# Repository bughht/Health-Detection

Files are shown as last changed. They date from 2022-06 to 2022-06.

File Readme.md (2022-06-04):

# 健康检测手环/手套
**一、项目的实施方案**

设计一个基于加速度传感器、陀螺仪、薄膜压力传感器、血氧传感器，开发可用于老龄化疾病(帕金森等)检测以及血氧饱和度等生理参数检测的系统。

设想1：老年人监测摔倒

当老年人遇到意外情况时,如果老年人质心位置—速度状态不在动态稳定区域以内(稳度为负)，老年人就会不稳定而失去平衡，对于老年人，下肢肌力衰退会导致下肢支撑力不够,不足以支撑起老年人在跌倒时导致的身体下降；同时由于老年人神经系统控制能力下降,神经传导减慢，动作反应时间延长,也会导致老年人在发生跌倒时不能及时的调整身体以保持平衡。

`	`老年人发生摔倒的过程中包括初始安全状态、失重状态、与低势物体或地面的撞击状态和倒后的平稳状态。其身体的三轴合加速度值定义为a=ax2+ay2+az2。在正常情况下，使用者的加速度值并不会有大的变化。但在失重状态和撞击状态，老年人的躯干三轴合加速度值a的变化很大。在日常生活中，人的上躯体部分的运动幅度较小，加速度变化不大，而在摔倒过程中，运动幅度变大，加速度变化很大。因此，三轴加速度传感器安装在老年人的上躯干部分。

设想2：帕金森监测

在出现帕金森之后，一些老年人的手脚会出现颤抖的情况，机械振荡是最简单导致震颤的原因，观察一个伸展的肢体如手，伸肌被激活去拮抗重力，而伸肌的激活又会导致拮抗它的屈肌激活，这样手部的肌纤维就会按照一个既定的频率被激活，因此手会依照一个既定的频率振荡，而这个频率在身体的不同部位是不同的，例如在手指是25Hz，手腕是6~8Hz，肘部是3~4Hz，而肩关节则是0.5~2Hz，这种频率会因为重量的加大而减低，或者紧张度的加大而增高。

用集成了三轴加速度计和陀螺仪的MPU-6050芯片采集手腕三轴加速度和角度，主要通过分析手腕三轴角度变化来判断穿戴者是否具有帕金森症状以及症状的严重程度。

设想3：血氧饱和度监测
`	`血氧饱和度是血液中被氧结合的氧合血红蛋白（HbO2）的容量占全部可结合的血红蛋白（Hb）容量的百分比，即血液中血氧的浓度，是呼吸循环的重要生理参数之一。如果血氧含量低，容易引发疲劳易困、精力不足、记忆力下降等状况，长期的血氧含量不足，还会对大脑、心脏等器官造成伤害。特别对于老年人，应每天监测血氧含量，一旦血氧低于警戒水平，需尽快补氧。
`	`测量时，需将血氧传感器紧贴皮肤。因为携带氧气的红血球能吸收较多红外光（850-1000mm），未携带氧气的红血球则是吸收较多的红光（600-750mm）。所以一般是通过测量双光束吸光度变化之比，一般选择入射光波长为660nm和940nm。运用Lambert-Bear定律并根据氧饱和度的定义可推出动脉血氧饱和度的近似公式为：Sa02=abQ。式中：Q为两种波长(Hb02、Hb)的吸光度变化之比a、b为常数，与仪器传感器结构、测量条件有关。 

**二、项目的核心器件**

**1.esp32开发板**

ESP-WROOM-32是一款通用型WiFi-BT-BLE MCU模组，功能强大，用途广泛。
`	`此款模组的核心是ESP32芯片，具有可扩展、自适应的特点。两个CPU核可以被单独控制或上电。时钟频率的调节范围为80MHz到240MHz。用户可以切断CPU的电源，利用低功耗协处理器来不断地监测外设的状态变化或某些模拟量是否超出阈值。ESP32还集成了丰富的外设，包括电容式触摸传感器、霍尔传感器、低噪声传感放大器，SD卡接口、以太网接口、高速SDIO／SPI、UART、I2S和I2C等。
`	`ESP-WROOM-32集成了传统蓝牙、低功耗蓝牙和Wi-Fi，具有广泛的用途：Wi-Fi支持极大范围的通信连接，也支持通过路由器直接连接互联网；而蓝牙可以让用户连接手机或者广播BLE Beacon以便于信号检测。ESP32芯片的睡眠电流小于5mA，使其适用于电池供电的可穿戴电子设备。ESP-WROOM-32支持的数据传输速率高达150Mbps，经过功率放大器后，输出功率可达到22dBm，可实现大范围的无线通信。因此，这款芯片拥有领先的技术规格，在高集成度、无线传输距离、功耗以及网络联通等方面性能佳。
`	`ESP32的操作系统是带有LWIP的freeRTOS，还内置了带有硬件加速功能的TLS1.2。芯片同时支持OTA加密升级。

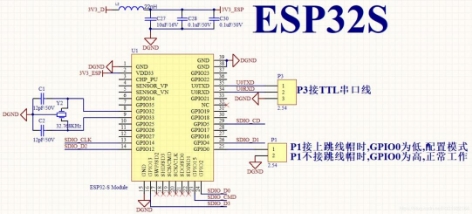
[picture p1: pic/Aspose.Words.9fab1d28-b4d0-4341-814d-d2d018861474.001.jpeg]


esp32电路图

2. **MPU6050**

MPU-60X0是世界上第一款集成 6 轴MotionTracking设备。它集成了3轴MEMS陀螺仪，3轴MEMS加速度计，以及一个可扩展的数字运动处理器 DMP（ DigitalMotion Processor），可用I2C接口连接一个第三方的数字传感器，比如磁力计。扩展之后就可以通过其 I2C或SPI接口输出一个9轴的信号（ SPI接口仅在MPU-6000可用）。 MPU-60X0也可以通过其I2C接口连接非惯性的数字传感器，比如压力传感器。
`	`MPU-60X0对陀螺仪和加速度计分别用了三个16位的ADC，将其测量的模拟量转化为可输出的数字量。为了精确跟踪快速和慢速的运动，传感器的测量范围都是用户可控的，陀螺仪可测范围为±250， ±500， ±1000， ±2000°/秒（ dps），加速度计可测范围为±2， ±4，±8， ±16g。
`	`MPU6050是一个比较常见的“陀螺仪”，实际上它不仅包含三轴陀螺仪，还包含了三轴加速度计。MPU6050是一个典型的MEMS，将六轴的东西集成到了大概3mm×3mm×1.5mm的体积之中，因此在飞控中得到广泛应用。

MPU6050使用I2C进行通信。I2C使用两条线SCL、SDA进行通信，再加上供电的两条线，使用MPU6050仅需要电源、GND、SCL、SDA即可。

其他引脚:

· XCL、XDA,一般是接其他I2C器件，如磁力计等，然后通过编程，可以让MPU6050帮你读取磁力计的数据，再一起读回单片机。

·IRQ，中断引脚，可以编程设定当数据准备好时，该引脚有电平变化，触发单片机的外部中断。

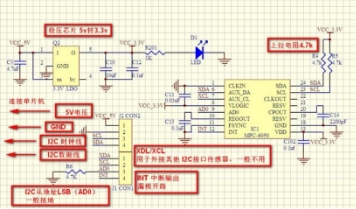
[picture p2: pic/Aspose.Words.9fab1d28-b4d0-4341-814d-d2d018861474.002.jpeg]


MPU6050电路图

**3.MAX30100**

MAX30100是一款集成有脉搏血氧仪和心率监测传感器的模块。该器件集成有两个LED、一个光电探测器，经过优化的光学器件和低噪声模拟信号处理器，可检测脉搏血氧及心率信号。MAX30100采用1.8V和3.3V的电源电压。可通过软件来关断电源，待机模式下的电流消耗量可忽略不计，因而可以始终保持电源连接。并且MAX30100采用I2C通信方式。

采集过程：RED和IR照射然后使用ADC进行数据采集，采集后的AD值经过数字滤波器进入数据寄存器，然后使用IIC进行数据采集，在转换AD值时，也可以采集温度值。

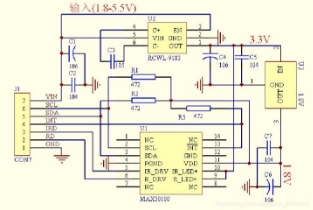
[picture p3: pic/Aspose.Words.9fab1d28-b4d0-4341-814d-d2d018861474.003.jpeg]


MAX30100电路图

**三、项目的制作过程**

考虑到手背血管相对贴近皮肤，有利于血氧传感器的监测，并且对于老年人手部帕金森震颤的监测更为容易，而若监测器件便于拆解，则可以让老人在出门时携带该器件以便监测老人在外是否摔倒，并在摔倒情况发生后尽快通知监护人，同时警示周围人群。

为了将上述方案融入一个检测系统中，且适合老人使用，我们决定制作一个可拆解的可穿戴式手部护具。

我们先进行硬件模块的设计与制作。为了实现我们预想的功能，我们首先选择并购置了相应的传感器；选用MPU6050收集使用者手部发生帕金森震颤时的三轴加速度和角度数据；用MAX30100检测使用者的血氧饱和度和体温；用薄膜压力传感器试图检测使用者手部挥动时对护具产生的压力，并与所测的三轴加速度和角度结合分析使用者是否摔倒。

一开始我们使用stm32进行环境开发，但由于需要与各模块相连接且需要将检测的数据传输到上位机，我们碰到了一些较难解决的问题，最后决定使用esp32开发环境。esp32开发板集成了蓝牙和WIFI传输数据的功能，简化了一些繁琐的配置步骤。理论上需要3.3V的电压供电，驱动各模块正常运行，但esp32自带前置降压，我们额外增加了一个升压模块将电源电压升高，再由esp32自己降到3.3V为各模块供电。

选择好各种传感器与开发板后，接下来就是将它们组装起来。利用I2C总线将各个模块与esp32进行连接。在实际焊接前，我们先在洞洞板上将各模块连接起来进行测试，得到了较为理想的结果。由于不会制作PCB板，在实际焊接过程中只能使用跳线将各模块进行连接。然而我们发现在实际焊接中并不能得到所预想的检测结果。经过检查发现是因为各模块是用导线进行连接的，导线较长对I2C会有较大的干扰。最终我们将导线剪短并加上了相应的上拉电阻，解决了此问题，成功将开发板与各模块相连。

1316718546-272481763-815E5E48DF970293284955976F0000EF

硬件各模块连接图

内部电路基本制作完成后，我们还需要设计一个外壳。起初，我们打算制作一个具有检测功能的手套，手腕部安装显示屏和血氧传感器，其余电路安置在手套的手背位置，仔细考虑一番觉得这样的设计不具有美观性且不切实际，最关键的是电路手背部分电路容易损坏，最终决定将所有电路全部装载在一个3D打印的外壳中，尽管这样的设计使成品看起来有一点笨重，但一体化设计使其具有很大的灵活性，不仅可以与各种模具结合以手表、护手等形式使用，也可以拆卸下来随身携带。

软件部分，我们起初打算采集到一个数据便将它传送至上位机处理，但由于我们之前将几个模块都连接在了I2C总线上，I2C是低速线，无法做到数据快速采集并传输。所以我们改为一帧里几个传感器同时采集数据，采集完将数据一起传输到上位机，但要提高采样率，保证较快的数据传输速度。处理采集到的数据时，我们使用了MATLAB，该软件运行处理较为缓慢，对我们项目正常的实施过程有一定的影响。

4. **项目的结果分析**

1.硬件电路板部分

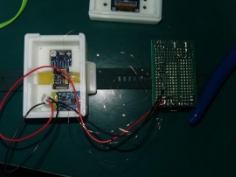
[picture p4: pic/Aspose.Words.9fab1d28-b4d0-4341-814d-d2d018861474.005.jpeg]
EA326454065DDD6A7FE0F28A32361031
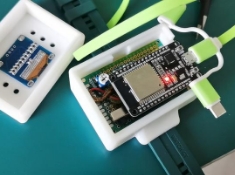
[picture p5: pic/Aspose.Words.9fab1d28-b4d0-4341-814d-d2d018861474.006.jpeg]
271CA8FF180BEBAEB58ACFB6554CEB21
       

2.最终成品分三段发送由三个模块采集的数据，每段128帧，第一段是由MPU6050采集的三轴加速度，使用卡尔曼计算姿态角，第二段使用MAX30100采集并计算血氧数据，第三段使用压力传感器采集施加至其上的压力，最后通过蓝牙将三段数据依次发送至上位机。

![1}4]48WX{49F(1C~1GFFUGF](pic/Aspose.Words.9fab1d28-b4d0-4341-814d-d2d018861474.007.jpeg)

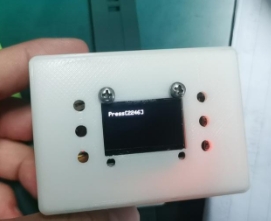
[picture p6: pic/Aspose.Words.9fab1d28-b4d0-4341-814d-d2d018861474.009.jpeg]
V60YQ6VU4)~8Q~AO)1K{V\_U
![5YYLY@]YP\_B7X8CJ}GT56LF](pic/Aspose.Words.9fab1d28-b4d0-4341-814d-d2d018861474.008.jpeg)   

3.当UI界面开始运行，点击开始检测，上位机程序会开放蓝牙接口并开始接收由硬件采集到的数据，并通过对采集到的数据进行分析，尽可能达到我们的设计目标。首先，当数据传输至上位机后对其进行分段处理，通过检测第一段采集到的加速度信号的过零率来分析佩戴者手部的震颤程度，以判断佩戴者手部是否出现类似帕金森的症状，并在界面右侧的静态文本框中显示“有帕金森吗小老弟”。通过对第二段采集到的血氧信号进行处理，得到佩戴者的血氧饱和度并对其频谱进行分析并显示至右侧上方两个坐标区中，同时，如果佩戴者的血氧不在阈值范围内，则判断佩戴者未正确佩戴手环，并显示在界面右侧第二个静态文本框中。对采集到的第三段压力数据进行处理并显示其频谱数据。

BC3344DD675796D992E37C8521789DD1

4. **总结与展望**

我们这次做出的成品总体来说还有许多不足之处，比如说预计的老人摔倒警报功能，由于我们的设计中是分三段采集和发送数据，而老人的摔倒是一个短时过程，可能老人摔倒时设备正好没有在监测老人的运动姿态，导致数据没有能够及时记录和传输，无法报警；同时我们还有能够计算温度的模块，但由于所需测定时间过长且干扰严重从而删除了该功能。

对于血氧数据的降噪技术也是一个难点，采集到的血氧数据没有得到很好的降噪，只能在比较严苛的操作情况下能看到有规律的qrs波尖峰上部图像，无法准确的计算心率。压力传感器的敏感度也偏低，没有达到预想的效果。

但是，从目前已实现的效果来看，它成功的发挥了一个帕金森手部震颤监测器的效果，且能够大致地测定使用者常态下的血氧饱和度，便携程度也达到了预想的标准，是一款兼具了巨大开发潜力和实用性为一身的作品。

在此基础上，我们对其更多功能的综合与优化也有其设想，例如：老年人可能出现记忆力降低或者患有老年痴呆的疾病，会有走失的风险。我们之后也可以在穿戴式设备上增加GPS实时定位的技术，随时了解老年人所在的位置。老年人身体机能下降，容易摔倒或突发某些疾病，出现上述情况时，不光通过警报通知周围人群，家属也可以及时定位到老人的所在位置。在表带附近增设血压监测传感器，及时发现老人的血压变动，提醒老人或其监护人及时服药或就医。

我们相信，如果能够继续优化开发，解决目前已发现的种种难题，那么，这将是一个兼具低成本、低使用要求、高效且实用的老年人监护辅助设备。	

**六、参考文献**

[1] 王亚宾,张小栋,穆小奇,韩焕杰.用于助老伴行机器人的老年人摔倒预测方法研究[J].电子测量与仪器学报,2018,32(07):1-7.

[2] Castiglia S F, Tatarelli A, Ranavolo A, et al. Ability of a set of trunk acceleration-derived 

gait stability indexes to identify gait unbalance and recurrent fallers in subjects with Parkinson's 

disease[J]. Journal of the Neurological Sciences, 2021, 429.

[3] 吴小玲,蔡桂艳.可穿戴式血氧传感器的设计和定标方法研究[J].生物医学工程学杂志,2009,26(04):731-734+738.

[4] 周一峰,刘超英,黄虎,郭一鸣,邹林方.基于光电容积脉搏波描记法的反射型PPG信号传感器的设计[J].电子世界,2016(12):161.

[5]       Zhou C, Yang L, Liao H, et al. Ankle foot motion recognition based on wireless wearable 

sEMG and acceleration sensors for smart AFO[J]. Sensors and Actuators A: Physical, 2021, 331: 113025.

[6] 吴天昊. 基于3轴加速度传感器及陀螺仪的老年人摔倒识别[D].北京工业大学,2013.

[7] Zhang Xiaodong,Wang Yunxia,Wei Xiaojuan.Research on control technology of elderly-assistant & walking-assistant robot based on tactile-slip sensation[J].Engineering Sciences,2013,11(01):89-96.

5

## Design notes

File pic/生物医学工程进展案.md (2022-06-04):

《生物医学工程进展A》课程项目

实施报告

题		 目：       穿戴式老年人生理参数检测设备     

组    号：                    1                   

任课教师：                 蒋皆恢                 

组    长： 19120318   洪浩天    24%               

成    员： 18121791   郭嘉      19%              

成    员： 19121718   詹美静    19%               

成    员： 19123227   刘奕欣    19%               

成    员： 19123248   胡悦滢    19%               

联系方式：            15800737097                 

二零二一年十一月九日 

**一、项目的实施方案**

设计一个基于加速度传感器、陀螺仪、薄膜压力传感器、血氧传感器，开发可用于老龄化疾病(帕金森等)检测以及血氧饱和度等生理参数检测的系统。

设想1：老年人监测摔倒

当老年人遇到意外情况时,如果老年人质心位置—速度状态不在动态稳定区域以内(稳度为负)，老年人就会不稳定而失去平衡，对于老年人，下肢肌力衰退会导致下肢支撑力不够,不足以支撑起老年人在跌倒时导致的身体下降；同时由于老年人神经系统控制能力下降,神经传导减慢，动作反应时间延长,也会导致老年人在发生跌倒时不能及时的调整身体以保持平衡。

`	`老年人发生摔倒的过程中包括初始安全状态、失重状态、与低势物体或地面的撞击状态和倒后的平稳状态。其身体的三轴合加速度值定义为a=ax2+ay2+az2。在正常情况下，使用者的加速度值并不会有大的变化。但在失重状态和撞击状态，老年人的躯干三轴合加速度值a的变化很大。在日常生活中，人的上躯体部分的运动幅度较小，加速度变化不大，而在摔倒过程中，运动幅度变大，加速度变化很大。因此，三轴加速度传感器安装在老年人的上躯干部分。

设想2：帕金森监测

在出现帕金森之后，一些老年人的手脚会出现颤抖的情况，机械振荡是最简单导致震颤的原因，观察一个伸展的肢体如手，伸肌被激活去拮抗重力，而伸肌的激活又会导致拮抗它的屈肌激活，这样手部的肌纤维就会按照一个既定的频率被激活，因此手会依照一个既定的频率振荡，而这个频率在身体的不同部位是不同的，例如在手指是25Hz，手腕是6~8Hz，肘部是3~4Hz，而肩关节则是0.5~2Hz，这种频率会因为重量的加大而减低，或者紧张度的加大而增高。

用集成了三轴加速度计和陀螺仪的MPU-6050芯片采集手腕三轴加速度和角度，主要通过分析手腕三轴角度变化来判断穿戴者是否具有帕金森症状以及症状的严重程度。

设想3：血氧饱和度监测
`	`血氧饱和度是血液中被氧结合的氧合血红蛋白（HbO2）的容量占全部可结合的血红蛋白（Hb）容量的百分比，即血液中血氧的浓度，是呼吸循环的重要生理参数之一。如果血氧含量低，容易引发疲劳易困、精力不足、记忆力下降等状况，长期的血氧含量不足，还会对大脑、心脏等器官造成伤害。特别对于老年人，应每天监测血氧含量，一旦血氧低于警戒水平，需尽快补氧。
`	`测量时，需将血氧传感器紧贴皮肤。因为携带氧气的红血球能吸收较多红外光（850-1000mm），未携带氧气的红血球则是吸收较多的红光（600-750mm）。所以一般是通过测量双光束吸光度变化之比，一般选择入射光波长为660nm和940nm。运用Lambert-Bear定律并根据氧饱和度的定义可推出动脉血氧饱和度的近似公式为：Sa02=abQ。式中：Q为两种波长(Hb02、Hb)的吸光度变化之比a、b为常数，与仪器传感器结构、测量条件有关。 

**二、项目的核心器件**

**1.esp32开发板**

ESP-WROOM-32是一款通用型WiFi-BT-BLE MCU模组，功能强大，用途广泛。
`	`此款模组的核心是ESP32芯片，具有可扩展、自适应的特点。两个CPU核可以被单独控制或上电。时钟频率的调节范围为80MHz到240MHz。用户可以切断CPU的电源，利用低功耗协处理器来不断地监测外设的状态变化或某些模拟量是否超出阈值。ESP32还集成了丰富的外设，包括电容式触摸传感器、霍尔传感器、低噪声传感放大器，SD卡接口、以太网接口、高速SDIO／SPI、UART、I2S和I2C等。
`	`ESP-WROOM-32集成了传统蓝牙、低功耗蓝牙和Wi-Fi，具有广泛的用途：Wi-Fi支持极大范围的通信连接，也支持通过路由器直接连接互联网；而蓝牙可以让用户连接手机或者广播BLE Beacon以便于信号检测。ESP32芯片的睡眠电流小于5mA，使其适用于电池供电的可穿戴电子设备。ESP-WROOM-32支持的数据传输速率高达150Mbps，经过功率放大器后，输出功率可达到22dBm，可实现大范围的无线通信。因此，这款芯片拥有领先的技术规格，在高集成度、无线传输距离、功耗以及网络联通等方面性能佳。
`	`ESP32的操作系统是带有LWIP的freeRTOS，还内置了带有硬件加速功能的TLS1.2。芯片同时支持OTA加密升级。

IMG\_256

esp32电路图

2. **MPU6050**

MPU-60X0是世界上第一款集成 6 轴MotionTracking设备。它集成了3轴MEMS陀螺仪，3轴MEMS加速度计，以及一个可扩展的数字运动处理器 DMP（ DigitalMotion Processor），可用I2C接口连接一个第三方的数字传感器，比如磁力计。扩展之后就可以通过其 I2C或SPI接口输出一个9轴的信号（ SPI接口仅在MPU-6000可用）。 MPU-60X0也可以通过其I2C接口连接非惯性的数字传感器，比如压力传感器。
`	`MPU-60X0对陀螺仪和加速度计分别用了三个16位的ADC，将其测量的模拟量转化为可输出的数字量。为了精确跟踪快速和慢速的运动，传感器的测量范围都是用户可控的，陀螺仪可测范围为±250， ±500， ±1000， ±2000°/秒（ dps），加速度计可测范围为±2， ±4，±8， ±16g。
`	`MPU6050是一个比较常见的“陀螺仪”，实际上它不仅包含三轴陀螺仪，还包含了三轴加速度计。MPU6050是一个典型的MEMS，将六轴的东西集成到了大概3mm×3mm×1.5mm的体积之中，因此在飞控中得到广泛应用。

MPU6050使用I2C进行通信。I2C使用两条线SCL、SDA进行通信，再加上供电的两条线，使用MPU6050仅需要电源、GND、SCL、SDA即可。

其他引脚:

· XCL、XDA,一般是接其他I2C器件，如磁力计等，然后通过编程，可以让MPU6050帮你读取磁力计的数据，再一起读回单片机。

·IRQ，中断引脚，可以编程设定当数据准备好时，该引脚有电平变化，触发单片机的外部中断。

IMG\_256

MPU6050电路图

**3.MAX30100**

MAX30100是一款集成有脉搏血氧仪和心率监测传感器的模块。该器件集成有两个LED、一个光电探测器，经过优化的光学器件和低噪声模拟信号处理器，可检测脉搏血氧及心率信号。MAX30100采用1.8V和3.3V的电源电压。可通过软件来关断电源，待机模式下的电流消耗量可忽略不计，因而可以始终保持电源连接。并且MAX30100采用I2C通信方式。

采集过程：RED和IR照射然后使用ADC进行数据采集，采集后的AD值经过数字滤波器进入数据寄存器，然后使用IIC进行数据采集，在转换AD值时，也可以采集温度值。

IMG\_256

MAX30100电路图

**三、项目的制作过程**

考虑到手背血管相对贴近皮肤，有利于血氧传感器的监测，并且对于老年人手部帕金森震颤的监测更为容易，而若监测器件便于拆解，则可以让老人在出门时携带该器件以便监测老人在外是否摔倒，并在摔倒情况发生后尽快通知监护人，同时警示周围人群。

为了将上述方案融入一个检测系统中，且适合老人使用，我们决定制作一个可拆解的可穿戴式手部护具。

我们先进行硬件模块的设计与制作。为了实现我们预想的功能，我们首先选择并购置了相应的传感器；选用MPU6050收集使用者手部发生帕金森震颤时的三轴加速度和角度数据；用MAX30100检测使用者的血氧饱和度和体温；用薄膜压力传感器试图检测使用者手部挥动时对护具产生的压力，并与所测的三轴加速度和角度结合分析使用者是否摔倒。

一开始我们使用stm32进行环境开发，但由于需要与各模块相连接且需要将检测的数据传输到上位机，我们碰到了一些较难解决的问题，最后决定使用esp32开发环境。esp32开发板集成了蓝牙和WIFI传输数据的功能，简化了一些繁琐的配置步骤。理论上需要3.3V的电压供电，驱动各模块正常运行，但esp32自带前置降压，我们额外增加了一个升压模块将电源电压升高，再由esp32自己降到3.3V为各模块供电。

选择好各种传感器与开发板后，接下来就是将它们组装起来。利用I2C总线将各个模块与esp32进行连接。在实际焊接前，我们先在洞洞板上将各模块连接起来进行测试，得到了较为理想的结果。由于不会制作PCB板，在实际焊接过程中只能使用跳线将各模块进行连接。然而我们发现在实际焊接中并不能得到所预想的检测结果。经过检查发现是因为各模块是用导线进行连接的，导线较长对I2C会有较大的干扰。最终我们将导线剪短并加上了相应的上拉电阻，解决了此问题，成功将开发板与各模块相连。

1316718546-272481763-815E5E48DF970293284955976F0000EF

硬件各模块连接图

内部电路基本制作完成后，我们还需要设计一个外壳。起初，我们打算制作一个具有检测功能的手套，手腕部安装显示屏和血氧传感器，其余电路安置在手套的手背位置，仔细考虑一番觉得这样的设计不具有美观性且不切实际，最关键的是电路手背部分电路容易损坏，最终决定将所有电路全部装载在一个3D打印的外壳中，尽管这样的设计使成品看起来有一点笨重，但一体化设计使其具有很大的灵活性，不仅可以与各种模具结合以手表、护手等形式使用，也可以拆卸下来随身携带。

软件部分，我们起初打算采集到一个数据便将它传送至上位机处理，但由于我们之前将几个模块都连接在了I2C总线上，I2C是低速线，无法做到数据快速采集并传输。所以我们改为一帧里几个传感器同时采集数据，采集完将数据一起传输到上位机，但要提高采样率，保证较快的数据传输速度。处理采集到的数据时，我们使用了MATLAB，该软件运行处理较为缓慢，对我们项目正常的实施过程有一定的影响。

4. **项目的结果分析**

1.硬件电路板部分

EA326454065DDD6A7FE0F28A32361031       271CA8FF180BEBAEB58ACFB6554CEB21

2.最终成品分三段发送由三个模块采集的数据，每段128帧，第一段是由MPU6050采集的三轴加速度，使用卡尔曼计算姿态角，第二段使用MAX30100采集并计算血氧数据，第三段使用压力传感器采集施加至其上的压力，最后通过蓝牙将三段数据依次发送至上位机。

![1}4]48WX{49F(1C~1GFFUGF](Aspose.Words.9fab1d28-b4d0-4341-814d-d2d018861474.007.jpeg)

![5YYLY@]YP\_B7X8CJ}GT56LF](Aspose.Words.9fab1d28-b4d0-4341-814d-d2d018861474.008.jpeg)   V60YQ6VU4)~8Q~AO)1K{V\_U

3.当UI界面开始运行，点击开始检测，上位机程序会开放蓝牙接口并开始接收由硬件采集到的数据，并通过对采集到的数据进行分析，尽可能达到我们的设计目标。首先，当数据传输至上位机后对其进行分段处理，通过检测第一段采集到的加速度信号的过零率来分析佩戴者手部的震颤程度，以判断佩戴者手部是否出现类似帕金森的症状，并在界面右侧的静态文本框中显示“有帕金森吗小老弟”。通过对第二段采集到的血氧信号进行处理，得到佩戴者的血氧饱和度并对其频谱进行分析并显示至右侧上方两个坐标区中，同时，如果佩戴者的血氧不在阈值范围内，则判断佩戴者未正确佩戴手环，并显示在界面右侧第二个静态文本框中。对采集到的第三段压力数据进行处理并显示其频谱数据。

BC3344DD675796D992E37C8521789DD1

4. **总结与展望**

我们这次做出的成品总体来说还有许多不足之处，比如说预计的老人摔倒警报功能，由于我们的设计中是分三段采集和发送数据，而老人的摔倒是一个短时过程，可能老人摔倒时设备正好没有在监测老人的运动姿态，导致数据没有能够及时记录和传输，无法报警；同时我们还有能够计算温度的模块，但由于所需测定时间过长且干扰严重从而删除了该功能。

对于血氧数据的降噪技术也是一个难点，采集到的血氧数据没有得到很好的降噪，只能在比较严苛的操作情况下能看到有规律的qrs波尖峰上部图像，无法准确的计算心率。压力传感器的敏感度也偏低，没有达到预想的效果。

但是，从目前已实现的效果来看，它成功的发挥了一个帕金森手部震颤监测器的效果，且能够大致地测定使用者常态下的血氧饱和度，便携程度也达到了预想的标准，是一款兼具了巨大开发潜力和实用性为一身的作品。

在此基础上，我们对其更多功能的综合与优化也有其设想，例如：老年人可能出现记忆力降低或者患有老年痴呆的疾病，会有走失的风险。我们之后也可以在穿戴式设备上增加GPS实时定位的技术，随时了解老年人所在的位置。老年人身体机能下降，容易摔倒或突发某些疾病，出现上述情况时，不光通过警报通知周围人群，家属也可以及时定位到老人的所在位置。在表带附近增设血压监测传感器，及时发现老人的血压变动，提醒老人或其监护人及时服药或就医。

我们相信，如果能够继续优化开发，解决目前已发现的种种难题，那么，这将是一个兼具低成本、低使用要求、高效且实用的老年人监护辅助设备。	

**六、参考文献**

1. 王亚宾,张小栋,穆小奇,韩焕杰.用于助老伴行机器人的老年人摔倒预测方法研究[J].电子测量与仪器学报,2018,32(07):1-7.

[2]           Castiglia S F, Tatarelli A, Ranavolo A, et al. Ability of a set of trunk acceleration-derived 

gait stability indexes to identify gait unbalance and recurrent fallers in subjects with Parkinson's 

disease[J]. Journal of the Neurological Sciences, 2021, 429.

[3] 吴小玲,蔡桂艳.可穿戴式血氧传感器的设计和定标方法研究[J].生物医学工程学杂志,2009,26(04):731-734+738.

[4] 周一峰,刘超英,黄虎,郭一鸣,邹林方.基于光电容积脉搏波描记法的反射型PPG信号传感器的设计[J].电子世界,2016(12):161.

[5]       Zhou C, Yang L, Liao H, et al. Ankle foot motion recognition based on wireless wearable 

sEMG and acceleration sensors for smart AFO[J]. Sensors and Actuators A: Physical, 2021, 331: 113025.

[6] 吴天昊. 基于3轴加速度传感器及陀螺仪的老年人摔倒识别[D].北京工业大学,2013.

[7] Zhang Xiaodong,Wang Yunxia,Wei Xiaojuan.Research on control technology of elderly-assistant & walking-assistant robot based on tactile-slip sensation[J].Engineering Sciences,2013,11(01):89-96.

5

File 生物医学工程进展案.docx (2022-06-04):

《生物医学工程进展A》课程项目

实施报告

题 目： 穿戴式老年人生理参数检测设备

组 号： 1

任课教师： 蒋皆恢

组 长： 19120318 洪浩天 24%

成 员： 18121791 郭嘉 19%

成 员： 19121718 詹美静 19%

成 员： 19123227 刘奕欣 19%

成 员： 19123248 胡悦滢 19%

联系方式： 15800737097

二零二一年十一月九日

一、项目的实施方案

设计一个基于加速度传感器、陀螺仪、薄膜压力传感器、血氧传感器，开发可用于老龄化疾病(帕金森等)检测以及血氧饱和度等生理参数检测的系统。

设想1：老年人监测摔倒

当老年人遇到意外情况时,如果老年人质心位置—速度状态不在动态稳定区域以内(稳度为负)，老年人就会不稳定而失去平衡，对于老年人，下肢肌力衰退会导致下肢支撑力不够,不足以支撑起老年人在跌倒时导致的身体下降；同时由于老年人神经系统控制能力下降,神经传导减慢，动作反应时间延长,也会导致老年人在发生跌倒时不能及时的调整身体以保持平衡。

老年人发生摔倒的过程中包括初始安全状态、失重状态、与低势物体或地面的撞击状态和倒后的平稳状态。其身体的三轴合加速度值定义为 a=√(a_x^2 +a_y^2 +a_z^2) 。在正常情况下，使用者的加速度值并不会有大的变化。但在失重状态和撞击状态，老年人的躯干三轴合加速度值a的变化很大。在日常生活中，人的上躯体部分的运动幅度较小，加速度变化不大，而在摔倒过程中，运动幅度变大，加速度变化很大。因此，三轴加速度传感器安装在老年人的上躯干部分。

设想2：帕金森监测

在出现帕金森之后，一些老年人的手脚会出现颤抖的情况，机械振荡是最简单导致震颤的原因，观察一个伸展的肢体如手，伸肌被激活去拮抗重力，而伸肌的激活又会导致拮抗它的屈肌激活，这样手部的肌纤维就会按照一个既定的频率被激活，因此手会依照一个既定的频率振荡，而这个频率在身体的不同部位是不同的，例如在手指是25Hz，手腕是6~8Hz，肘部是3~4Hz，而肩关节则是0.5~2Hz，这种频率会因为重量的加大而减低，或者紧张度的加大而增高。

用集成了三轴加速度计和陀螺仪的MPU-6050芯片采集手腕三轴加速度和角度，主要通过分析手腕三轴角度变化来判断穿戴者是否具有帕金森症状以及症状的严重程度。

设想3：血氧饱和度监测
血氧饱和度是血液中被氧结合的氧合血红蛋白（HbO2）的容量占全部可结合的血红蛋白（Hb）容量的百分比，即血液中血氧的浓度，是呼吸循环的重要生理参数之一。如果血氧含量低，容易引发疲劳易困、精力不足、记忆力下降等状况，长期的血氧含量不足，还会对大脑、心脏等器官造成伤害。特别对于老年人，应每天监测血氧含量，一旦血氧低于警戒水平，需尽快补氧。
测量时，需将血氧传感器紧贴皮肤。因为携带氧气的红血球能吸收较多红外光（850-1000mm），未携带氧气的红血球则是吸收较多的红光（600-750mm）。所以一般是通过测量双光束吸光度变化之比，一般选择入射光波长为660nm和940nm。运用Lambert-Bear定律并根据氧饱和度的定义可推出动脉血氧饱和度的近似公式为：Sa02=abQ。式中：Q为两种波长(Hb02、Hb)的吸光度变化之比a、b为常数，与仪器传感器结构、测量条件有关。

二、项目的核心器件

1.esp32开发板

ESP-WROOM-32是一款通用型WiFi-BT-BLE MCU模组，功能强大，用途广泛。
此款模组的核心是ESP32芯片，具有可扩展、自适应的特点。两个CPU核可以被单独控制或上电。时钟频率的调节范围为80MHz到240MHz。用户可以切断CPU的电源，利用低功耗协处理器来不断地监测外设的状态变化或某些模拟量是否超出阈值。ESP32还集成了丰富的外设，包括电容式触摸传感器、霍尔传感器、低噪声传感放大器，SD卡接口、以太网接口、高速SDIO／SPI、UART、I2S和I2C等。
ESP-WROOM-32集成了传统蓝牙、低功耗蓝牙和Wi-Fi，具有广泛的用途：Wi-Fi支持极大范围的通信连接，也支持通过路由器直接连接互联网；而蓝牙可以让用户连接手机或者广播BLE Beacon以便于信号检测。ESP32芯片的睡眠电流小于5mA，使其适用于电池供电的可穿戴电子设备。ESP-WROOM-32支持的数据传输速率高达150Mbps，经过功率放大器后，输出功率可达到22dBm，可实现大范围的无线通信。因此，这款芯片拥有领先的技术规格，在高集成度、无线传输距离、功耗以及网络联通等方面性能佳。
ESP32的操作系统是带有LWIP的freeRTOS，还内置了带有硬件加速功能的TLS1.2。芯片同时支持OTA加密升级。

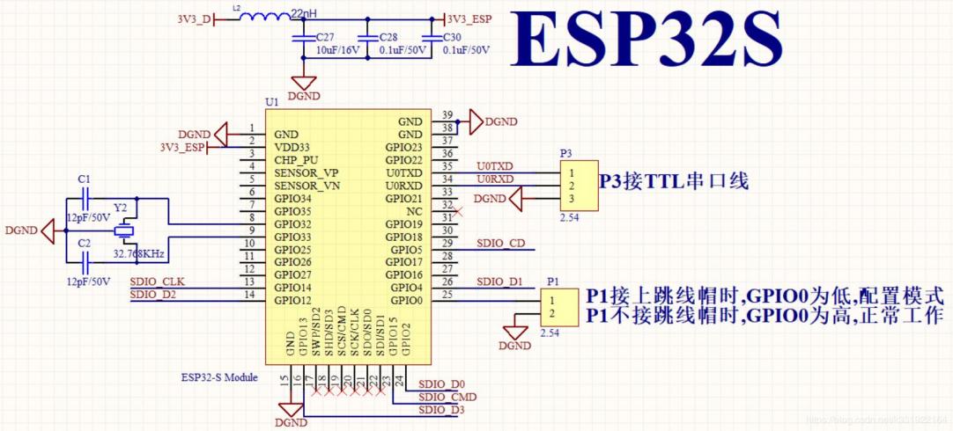
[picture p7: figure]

esp32电路图

2. MPU6050

MPU-60X0是世界上第一款集成 6 轴MotionTracking设备。它集成了3轴MEMS陀螺仪，3轴MEMS加速度计，以及一个可扩展的数字运动处理器 DMP（ DigitalMotion Processor），可用I2C接口连接一个第三方的数字传感器，比如磁力计。扩展之后就可以通过其 I2C或SPI接口输出一个9轴的信号（ SPI接口仅在MPU-6000可用）。 MPU-60X0也可以通过其I2C接口连接非惯性的数字传感器，比如压力传感器。
MPU-60X0对陀螺仪和加速度计分别用了三个16位的ADC，将其测量的模拟量转化为可输出的数字量。为了精确跟踪快速和慢速的运动，传感器的测量范围都是用户可控的，陀螺仪可测范围为±250， ±500， ±1000， ±2000°/秒（ dps），加速度计可测范围为±2， ±4，±8， ±16g。
MPU6050是一个比较常见的“陀螺仪”，实际上它不仅包含三轴陀螺仪，还包含了三轴加速度计。MPU6050是一个典型的MEMS，将六轴的东西集成到了大概3mm×3mm×1.5mm的体积之中，因此在飞控中得到广泛应用。

MPU6050使用I2C进行通信。I2C使用两条线SCL、SDA进行通信，再加上供电的两条线，使用MPU6050仅需要电源、GND、SCL、SDA即可。

其他引脚:

· XCL、XDA,一般是接其他I2C器件，如磁力计等，然后通过编程，可以让MPU6050帮你读取磁力计的数据，再一起读回单片机。

·IRQ，中断引脚，可以编程设定当数据准备好时，该引脚有电平变化，触发单片机的外部中断。

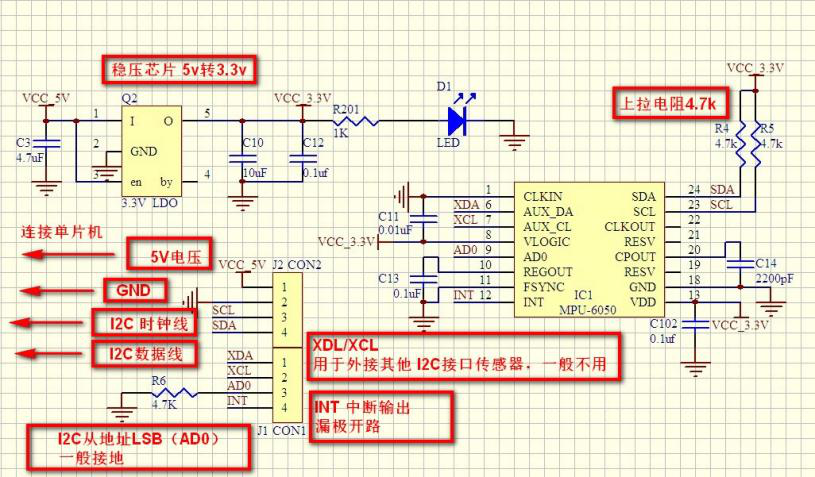
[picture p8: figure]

MPU6050电路图

3.MAX30100

MAX30100是一款集成有脉搏血氧仪和心率监测传感器的模块。该器件集成有两个LED、一个光电探测器，经过优化的光学器件和低噪声模拟信号处理器，可检测脉搏血氧及心率信号。MAX30100采用1.8V和3.3V的电源电压。可通过软件来关断电源，待机模式下的电流消耗量可忽略不计，因而可以始终保持电源连接。并且MAX30100采用I2C通信方式。

采集过程：RED和IR照射然后使用ADC进行数据采集，采集后的AD值经过数字滤波器进入数据寄存器，然后使用IIC进行数据采集，在转换AD值时，也可以采集温度值。

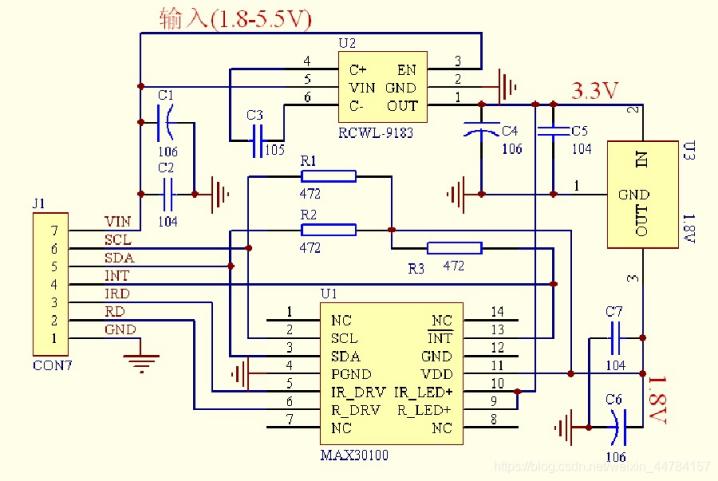
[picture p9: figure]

MAX30100电路图

三、项目的制作过程

考虑到手背血管相对贴近皮肤，有利于血氧传感器的监测，并且对于老年人手部帕金森震颤的监测更为容易，而若监测器件便于拆解，则可以让老人在出门时携带该器件以便监测老人在外是否摔倒，并在摔倒情况发生后尽快通知监护人，同时警示周围人群。

为了将上述方案融入一个检测系统中，且适合老人使用，我们决定制作一个可拆解的可穿戴式手部护具。

我们先进行硬件模块的设计与制作。为了实现我们预想的功能，我们首先选择并购置了相应的传感器；选用MPU6050收集使用者手部发生帕金森震颤时的三轴加速度和角度数据；用MAX30100检测使用者的血氧饱和度和体温；用薄膜压力传感器试图检测使用者手部挥动时对护具产生的压力，并与所测的三轴加速度和角度结合分析使用者是否摔倒。

一开始我们使用stm32进行环境开发，但由于需要与各模块相连接且需要将检测的数据传输到上位机，我们碰到了一些较难解决的问题，最后决定使用esp32开发环境。esp32开发板集成了蓝牙和WIFI传输数据的功能，简化了一些繁琐的配置步骤。理论上需要3.3V的电压供电，驱动各模块正常运行，但esp32自带前置降压，我们额外增加了一个升压模块将电源电压升高，再由esp32自己降到3.3V为各模块供电。

选择好各种传感器与开发板后，接下来就是将它们组装起来。利用I2C总线将各个模块与esp32进行连接。在实际焊接前，我们先在洞洞板上将各模块连接起来进行测试，得到了较为理想的结果。由于不会制作PCB板，在实际焊接过程中只能使用跳线将各模块进行连接。然而我们发现在实际焊接中并不能得到所预想的检测结果。经过检查发现是因为各模块是用导线进行连接的，导线较长对I2C会有较大的干扰。最终我们将导线剪短并加上了相应的上拉电阻，解决了此问题，成功将开发板与各模块相连。

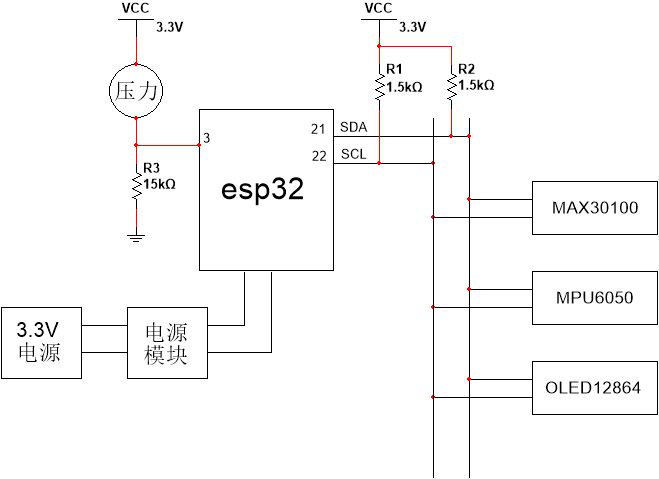
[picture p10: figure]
1316718546-272481763-815E5E48DF970293284955976F0000EF

硬件各模块连接图

内部电路基本制作完成后，我们还需要设计一个外壳。起初，我们打算制作一个具有检测功能的手套，手腕部安装显示屏和血氧传感器，其余电路安置在手套的手背位置，仔细考虑一番觉得这样的设计不具有美观性且不切实际，最关键的是电路手背部分电路容易损坏，最终决定将所有电路全部装载在一个3D打印的外壳中，尽管这样的设计使成品看起来有一点笨重，但一体化设计使其具有很大的灵活性，不仅可以与各种模具结合以手表、护手等形式使用，也可以拆卸下来随身携带。

软件部分，我们起初打算采集到一个数据便将它传送至上位机处理，但由于我们之前将几个模块都连接在了I2C总线上，I2C是低速线，无法做到数据快速采集并传输。所以我们改为一帧里几个传感器同时采集数据，采集完将数据一起传输到上位机，但要提高采样率，保证较快的数据传输速度。处理采集到的数据时，我们使用了MATLAB，该软件运行处理较为缓慢，对我们项目正常的实施过程有一定的影响。

4、 项目的结果分析

1.硬件电路板部分

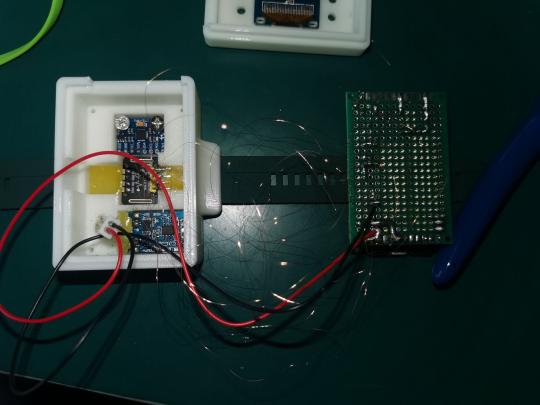
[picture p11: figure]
EA326454065DDD6A7FE0F28A32361031
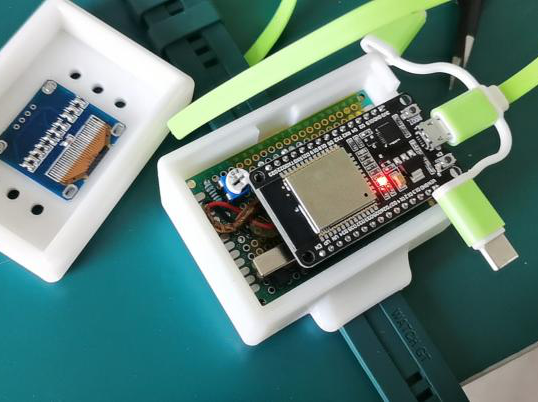
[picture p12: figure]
271CA8FF180BEBAEB58ACFB6554CEB21

2.最终成品分三段发送由三个模块采集的数据，每段128帧，第一段是由MPU6050采集的三轴加速度，使用卡尔曼计算姿态角，第二段使用MAX30100采集并计算血氧数据，第三段使用压力传感器采集施加至其上的压力，最后通过蓝牙将三段数据依次发送至上位机。

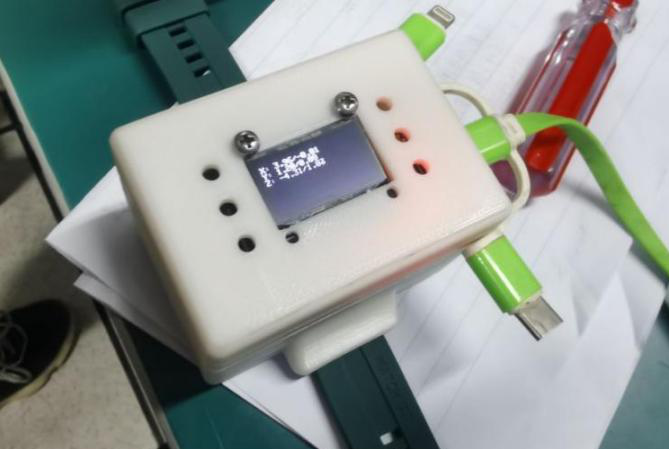
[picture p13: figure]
1}4]48WX{49F(1C~1GFFUGF
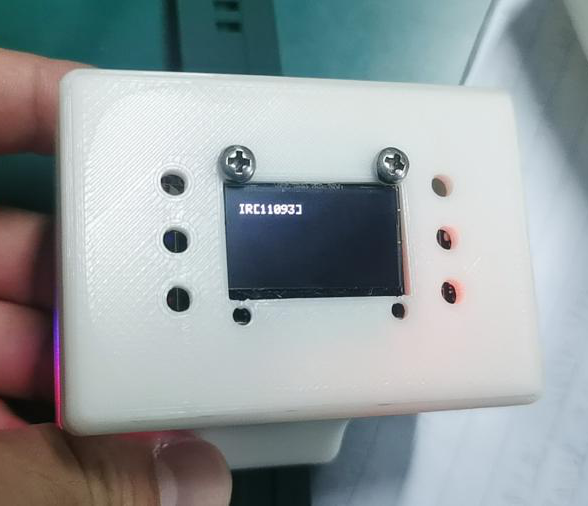
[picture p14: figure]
5YYLY@]YP_B7X8CJ}GT56LF
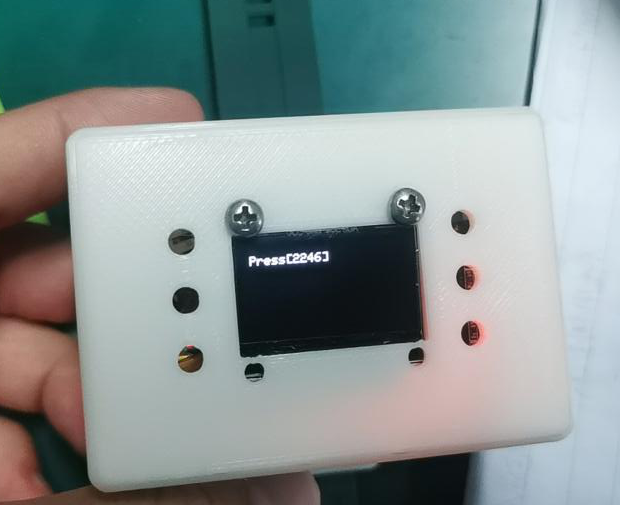
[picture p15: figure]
V60YQ6VU4)~8Q~AO)1K{V_U

3.当UI界面开始运行，点击开始检测，上位机程序会开放蓝牙接口并开始接收由硬件采集到的数据，并通过对采集到的数据进行分析，尽可能达到我们的设计目标。首先，当数据传输至上位机后对其进行分段处理，通过检测第一段采集到的加速度信号的过零率来分析佩戴者手部的震颤程度，以判断佩戴者手部是否出现类似帕金森的症状，并在界面右侧的静态文本框中显示“有帕金森吗小老弟”。通过对第二段采集到的血氧信号进行处理，得到佩戴者的血氧饱和度并对其频谱进行分析并显示至右侧上方两个坐标区中，同时，如果佩戴者的血氧不在阈值范围内，则判断佩戴者未正确佩戴手环，并显示在界面右侧第二个静态文本框中。对采集到的第三段压力数据进行处理并显示其频谱数据。

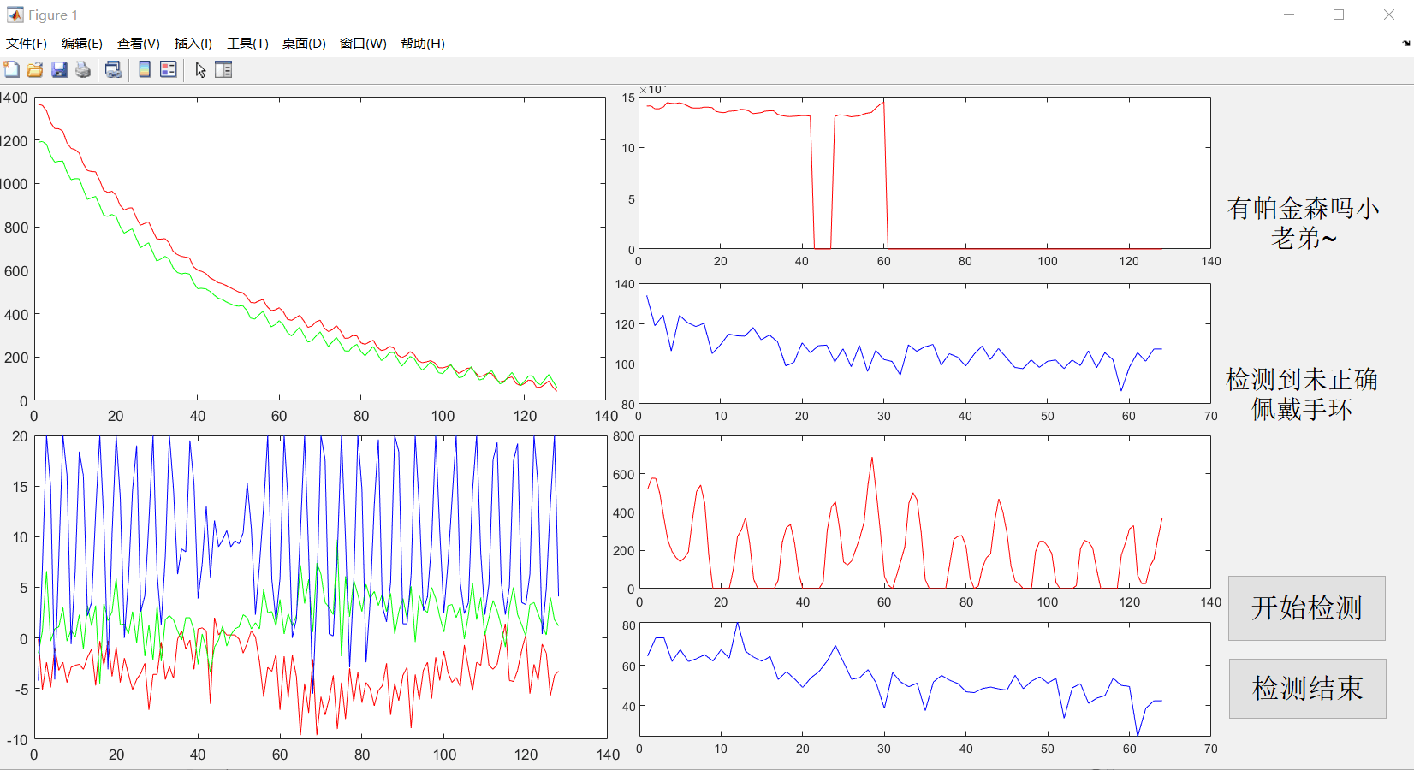
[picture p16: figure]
BC3344DD675796D992E37C8521789DD1

5、 总结与展望

我们这次做出的成品总体来说还有许多不足之处，比如说预计的老人摔倒警报功能，由于我们的设计中是分三段采集和发送数据，而老人的摔倒是一个短时过程，可能老人摔倒时设备正好没有在监测老人的运动姿态，导致数据没有能够及时记录和传输，无法报警；同时我们还有能够计算温度的模块，但由于所需测定时间过长且干扰严重从而删除了该功能。

对于血氧数据的降噪技术也是一个难点，采集到的血氧数据没有得到很好的降噪，只能在比较严苛的操作情况下能看到有规律的qrs波尖峰上部图像，无法准确的计算心率。压力传感器的敏感度也偏低，没有达到预想的效果。

但是，从目前已实现的效果来看，它成功的发挥了一个帕金森手部震颤监测器的效果，且能够大致地测定使用者常态下的血氧饱和度，便携程度也达到了预想的标准，是一款兼具了巨大开发潜力和实用性为一身的作品。

在此基础上，我们对其更多功能的综合与优化也有其设想，例如：老年人可能出现记忆力降低或者患有老年痴呆的疾病，会有走失的风险。我们之后也可以在穿戴式设备上增加GPS实时定位的技术，随时了解老年人所在的位置。老年人身体机能下降，容易摔倒或突发某些疾病，出现上述情况时，不光通过警报通知周围人群，家属也可以及时定位到老人的所在位置。在表带附近增设血压监测传感器，及时发现老人的血压变动，提醒老人或其监护人及时服药或就医。

我们相信，如果能够继续优化开发，解决目前已发现的种种难题，那么，这将是一个兼具低成本、低使用要求、高效且实用的老年人监护辅助设备。

六、参考文献

[1] 王亚宾,张小栋,穆小奇,韩焕杰.用于助老伴行机器人的老年人摔倒预测方法研究[J].电子测量与仪器学报,2018,32(07):1-7.

[2] Castiglia S F, Tatarelli A, Ranavolo A, et al. Ability of a set of trunk acceleration-derived

gait stability indexes to identify gait unbalance and recurrent fallers in subjects with Parkinson's

disease[J]. Journal of the Neurological Sciences, 2021, 429.

[3] 吴小玲,蔡桂艳.可穿戴式血氧传感器的设计和定标方法研究[J].生物医学工程学杂志,2009,26(04):731-734+738.

[4] 周一峰,刘超英,黄虎,郭一鸣,邹林方.基于光电容积脉搏波描记法的反射型PPG信号传感器的设计[J].电子世界,2016(12):161.

[5] Zhou C, Yang L, Liao H, et al. Ankle foot motion recognition based on wireless wearable

sEMG and acceleration sensors for smart AFO[J]. Sensors and Actuators A: Physical, 2021, 331: 113025.

[6] 吴天昊. 基于3轴加速度传感器及陀螺仪的老年人摔倒识别[D].北京工业大学,2013.

[7] Zhang Xiaodong,Wang Yunxia,Wei Xiaojuan.Research on control technology of elderly-assistant & walking-assistant robot based on tactile-slip sensation[J].Engineering Sciences,2013,11(01):89-96.

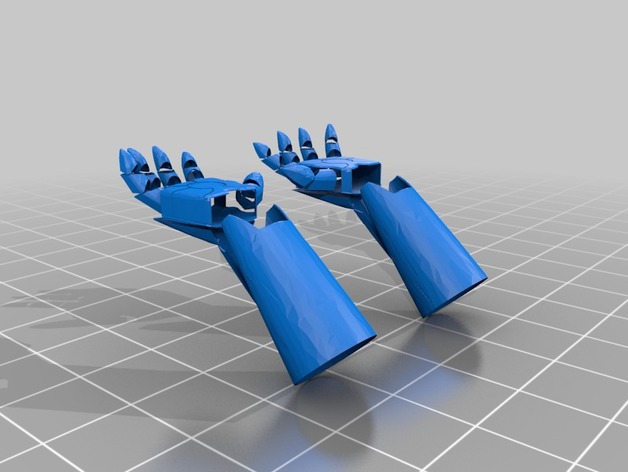
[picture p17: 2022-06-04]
glove/temp/images/20fae097e2fad64cbdc021344853d4c9_preview_featured.jpg

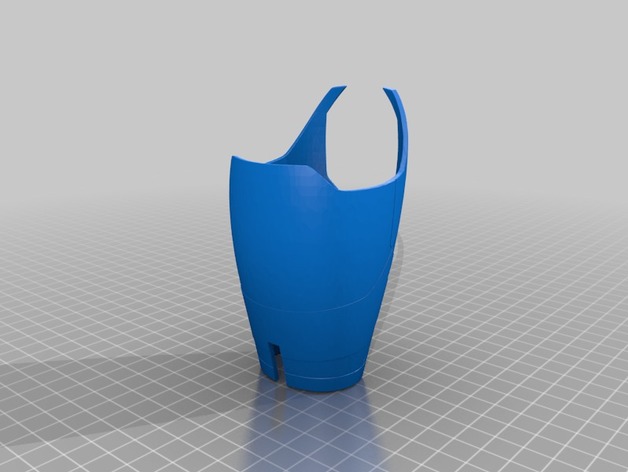
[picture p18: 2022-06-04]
glove/temp/images/f26903fb27486556618ea778fd6b1efe_preview_featured.jpg

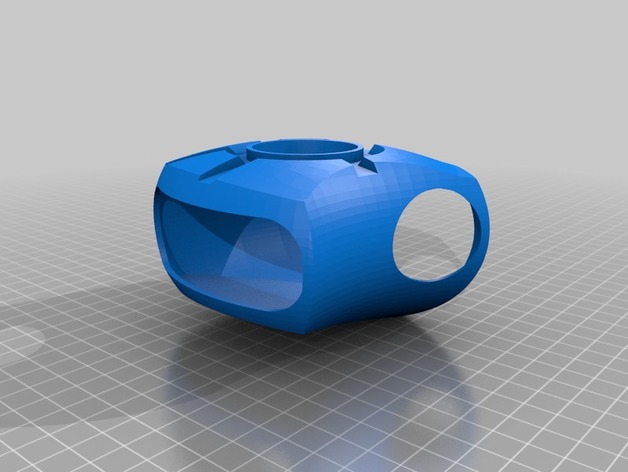
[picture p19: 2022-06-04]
glove/temp/images/5aa3b4d2776f7bed10a7a8cf8550a3e7_preview_featured.jpg

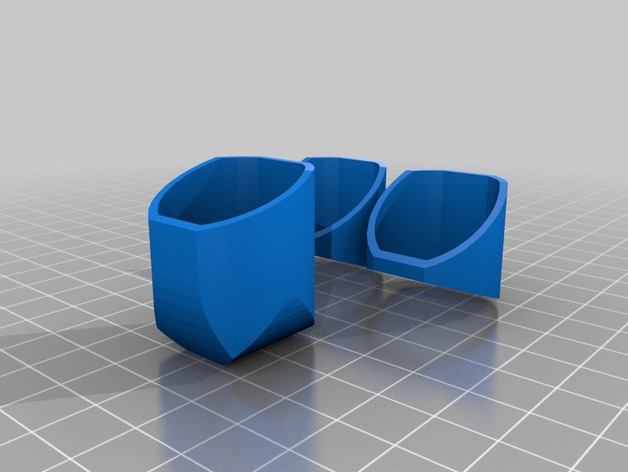
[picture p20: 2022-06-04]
glove/temp/images/92da67f24968c3ef75bc014f78401717_preview_featured.jpg

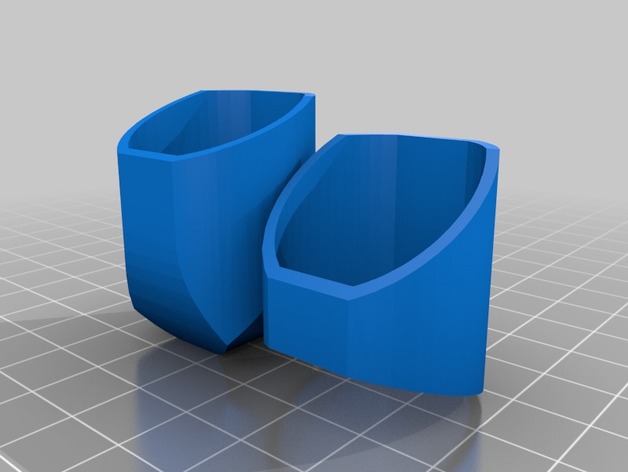
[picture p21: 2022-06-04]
glove/temp/images/585fdc3436375e2d550339d3e533fe1f_preview_featured.jpg

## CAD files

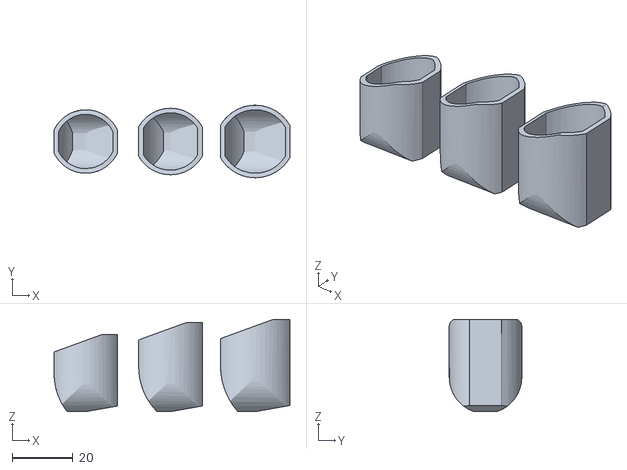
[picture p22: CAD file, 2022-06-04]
glove/temp/files/Untitled-5a9839b9.stl
78.0 x 24.0 x 30.5

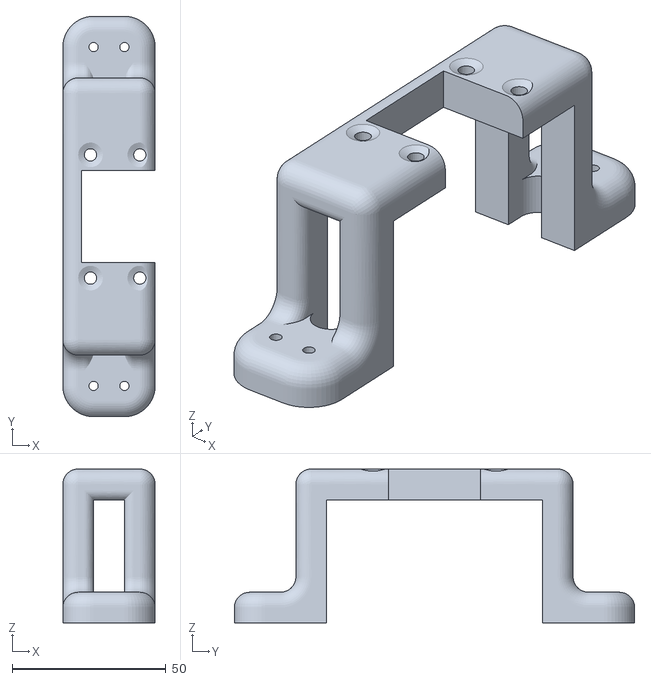
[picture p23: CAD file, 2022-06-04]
Model_out_1.stl
30.0 x 130.0 x 50.0

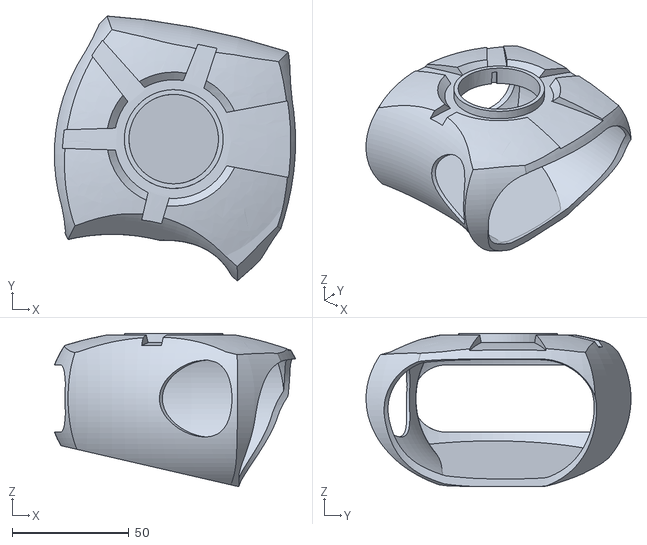
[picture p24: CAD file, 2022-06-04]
glove/temp/files/Untitled-5a9838f2.stl
103.5 x 113.7 x 65.9

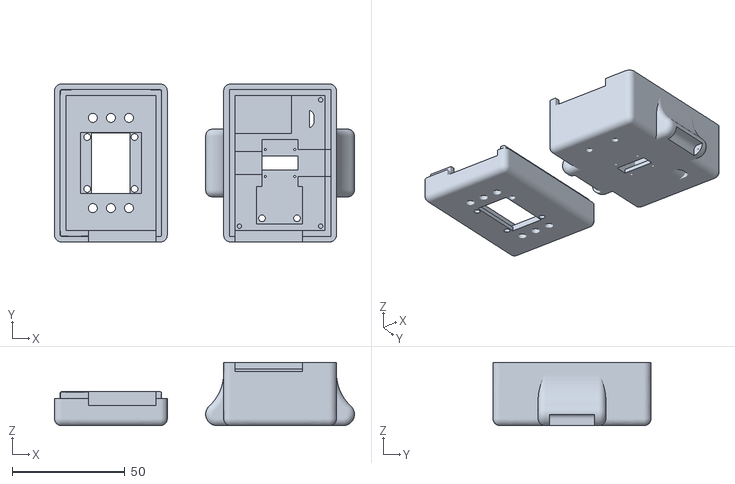
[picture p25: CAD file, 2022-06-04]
Model_Watch_V2_Plus.stl
133.0 x 70.0 x 28.0

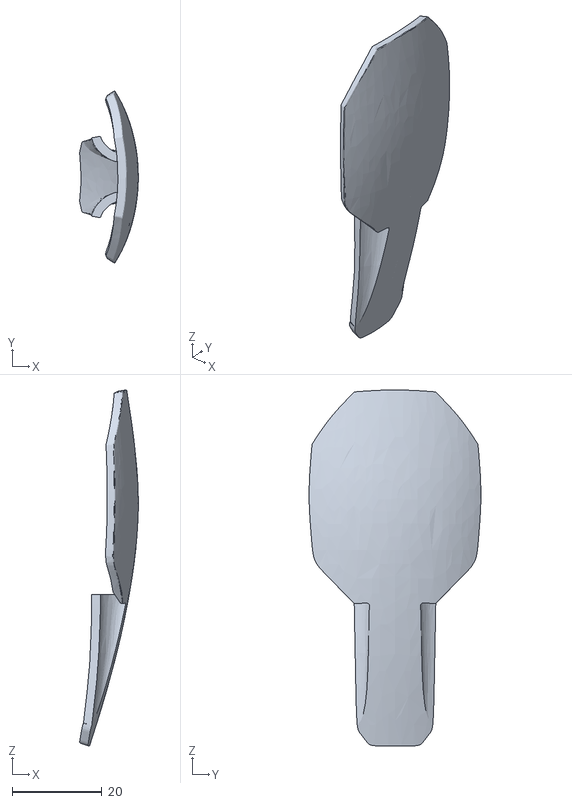
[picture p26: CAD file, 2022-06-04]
glove/temp/files/Untitled-5a983961.stl
13.0 x 38.2 x 79.2

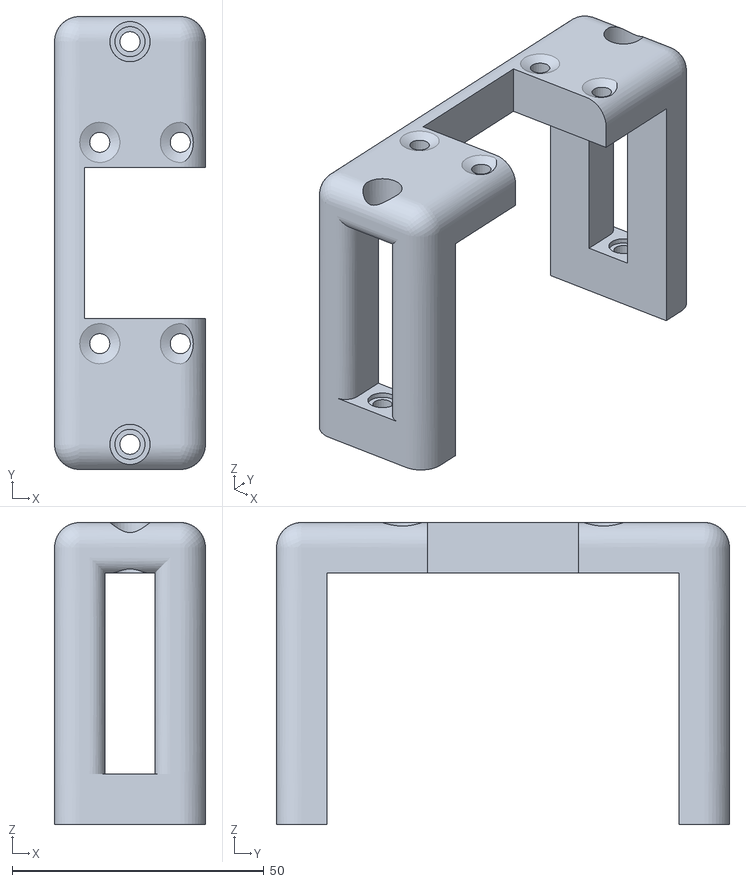
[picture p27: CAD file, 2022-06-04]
Model_out_2.stl
30.0 x 90.0 x 60.0

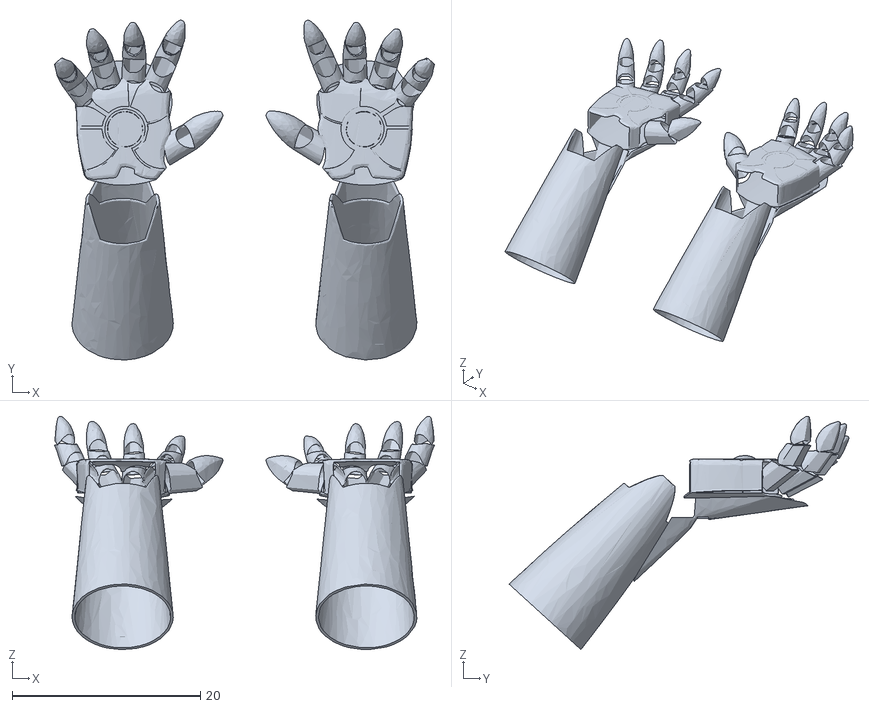
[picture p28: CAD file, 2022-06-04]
glove/temp/files/Untitled-5a983ed1.stl
40.4 x 36.1 x 24.8

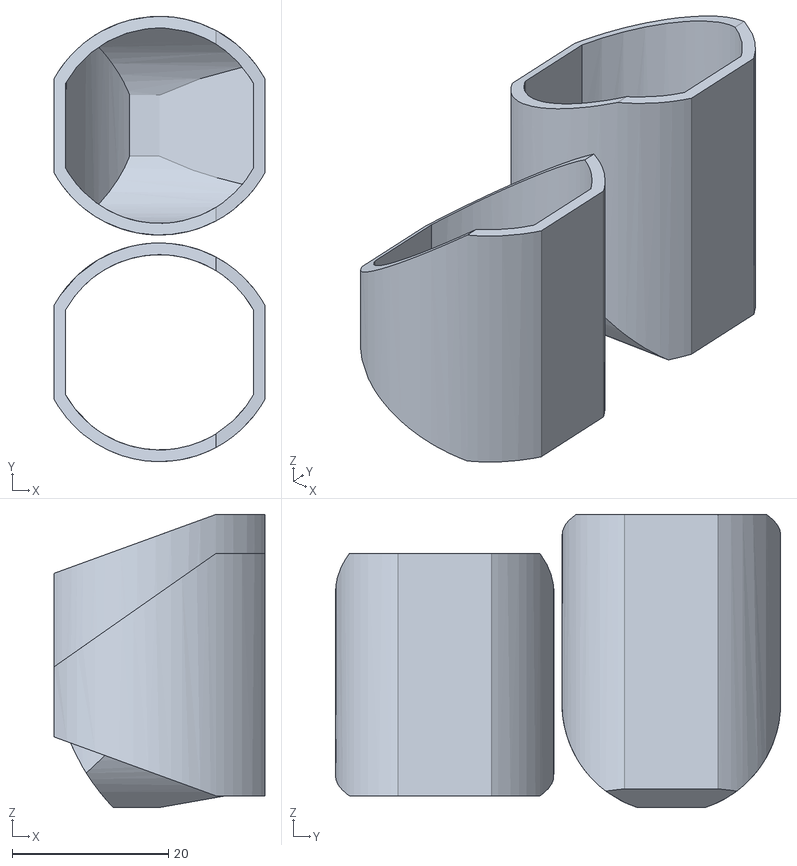
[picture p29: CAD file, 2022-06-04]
glove/temp/files/Untitled-5a9839ae.stl
27.0 x 57.0 x 37.5

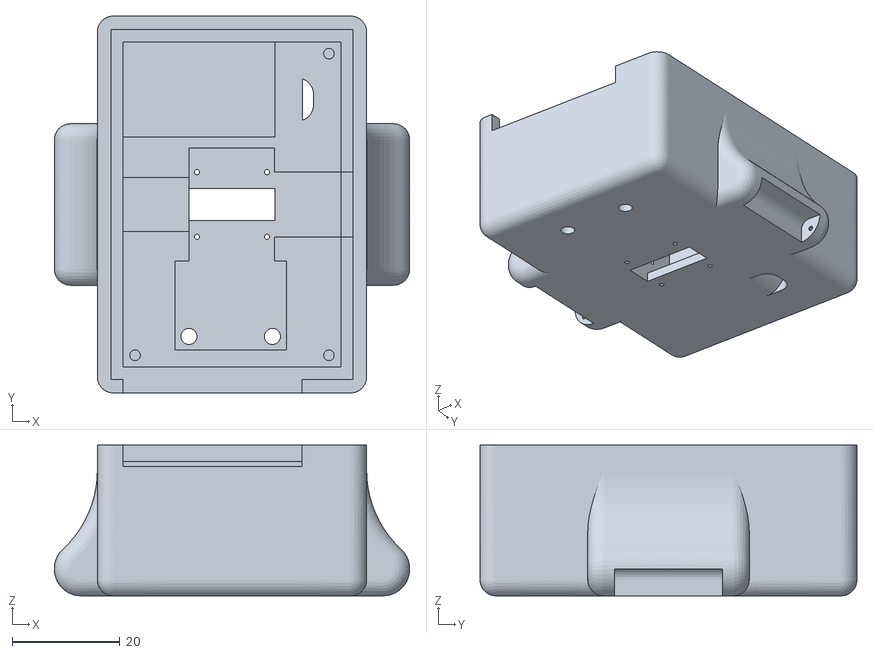
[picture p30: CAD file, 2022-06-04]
Model_Watch_V3.stl
66.0 x 70.0 x 28.0

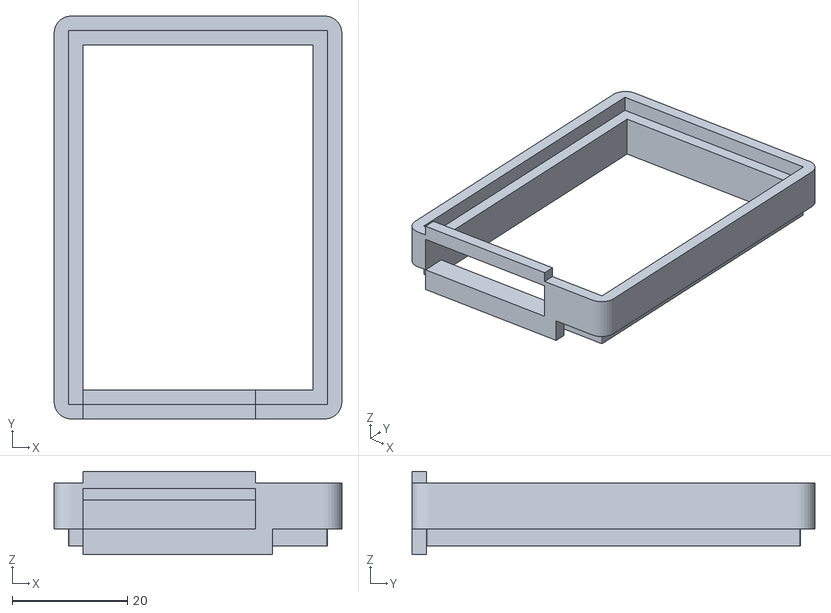
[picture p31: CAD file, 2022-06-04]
adder.stl
50.0 x 70.0 x 14.5

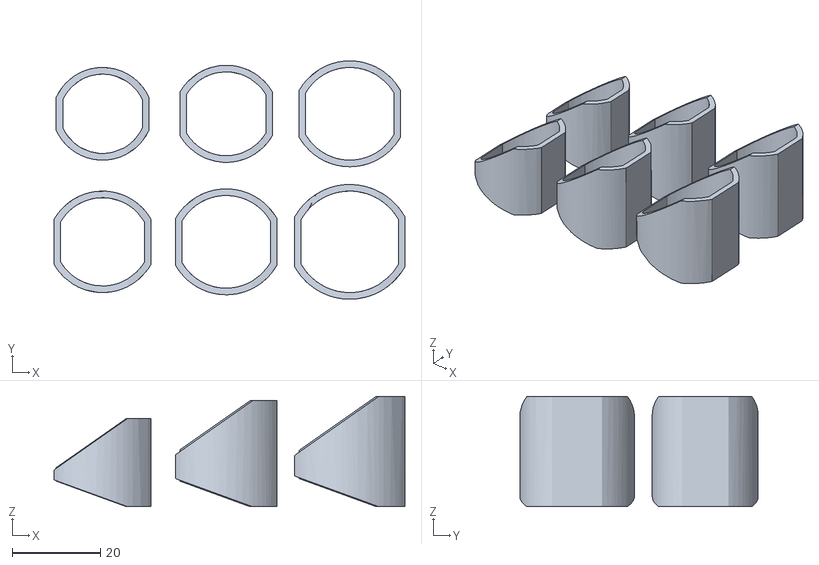
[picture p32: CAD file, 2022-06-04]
glove/temp/files/Untitled-5a9839a3.stl
79.5 x 54.0 x 25.0

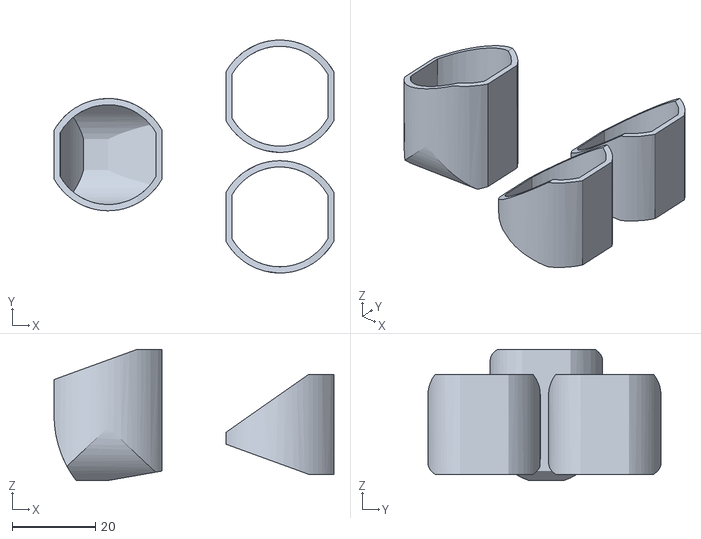
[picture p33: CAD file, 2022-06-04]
glove/temp/files/Untitled-5a9839c6.stl
67.3 x 56.0 x 31.5

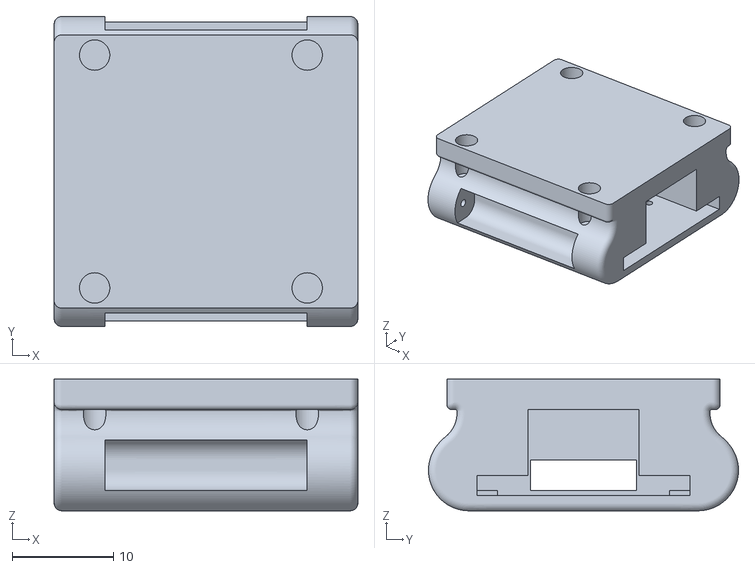
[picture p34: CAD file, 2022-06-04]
Model_Watch.stl
30.0 x 30.6 x 13.0

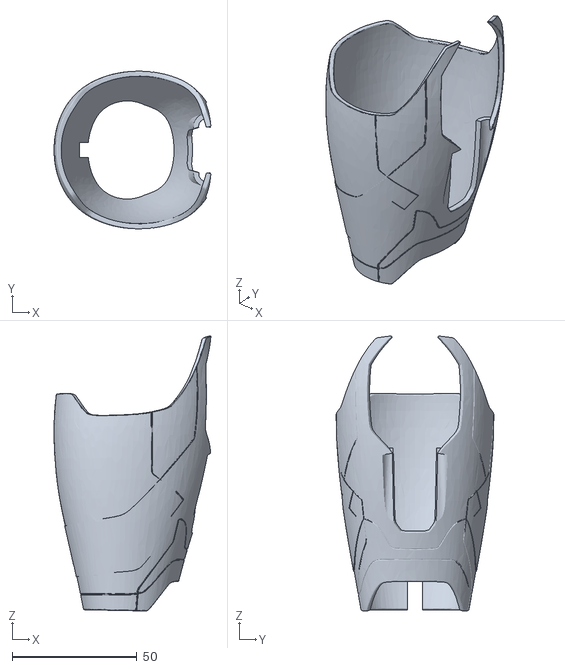
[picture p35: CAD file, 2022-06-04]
glove/temp/files/Untitled-5a98394b.stl
62.9 x 63.2 x 110.2

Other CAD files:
GLOVE.stl

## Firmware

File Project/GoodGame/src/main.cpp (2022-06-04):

#include <Arduino.h>
#include <MPU6050_tockn.h>
#include <MAX30105.h>
#include <heartRate.h>
#include <Wire.h>
#include <Adafruit_GFX.h>
#include <Adafruit_SSD1306.h>
#include "BluetoothSerial.h"

#define SDA 21
#define SCL 22
#define OLED_RESET 4

#define BUFFERLEN 128

#if !defined(CONFIG_BT_ENABLED) || !defined(CONFIG_BLUEDROID_ENABLED)
#error Bluetooth is not enabled! Please run `make menuconfig` to and enable it
#endif

MPU6050 mpu6050(Wire);
MAX30105 particleSensor;
long timer = 0, loctime;
float AngleX, AngleY, AngleZ;
Adafruit_SSD1306 display(128, 64, &Wire, OLED_RESET);
const byte RATE_SIZE = 4; //Increase this for more averaging. 4 is good.
byte rates[RATE_SIZE];    //Array of heart rates
byte rateSpot = 0;
long lastBeat = 0; //Time at which the last beat occurred

float beatsPerMinute = 60;
int beatAvg = 60;
int COUNT = 0;

long irValue;

long MPU_starttime, MPU_endtime;
double MPU_fps = 30.0;
float MPU_DATA[6][BUFFERLEN];

long MAX_starttime, MAX_endtime;
double MAX_fps = 30.0;
uint32_t MAX_IR_DATA[BUFFERLEN];

long Press_starttime, Press_endtime;
double Press_fps = 30.0;
uint16_t Press_DATA[BUFFERLEN];

BluetoothSerial SerialBT;

String bluetooth_in_buffer = "";

void Draw_Init_Interface(void)
{
    for (size_t i = 0; i < 46; i = i + 5)
    {
        display.clearDisplay();
        display.setTextSize(1);
        display.setTextColor(WHITE);
        display.setCursor(25, 20);
        display.println("Initialize...");
        display.drawRect(38, 38, 51, 6, WHITE);      //以（38，38）为起点绘制一个长度51宽度为6的矩形
        display.drawLine(40, 40, 40 + i, 40, WHITE); //循环绘制线条达到显示进度的效果
        display.drawLine(40, 41, 40 + i, 41, WHITE);
        display.display();
        delay(100);
        display.clearDisplay();
    }
    display.display();
}

void setup()
{
    Wire.begin(SDA, SCL);
    Serial.begin(115200);
    SerialBT.begin("SmartD");

    mpu6050.begin();
    mpu6050.calcGyroOffsets(true);

    if (particleSensor.begin(Wire, I2C_SPEED_FAST) == false) //Use default I2C port, 400kHz speed
    {
        Serial.println("MAX30105 was not found. Please check wiring/power. ");
    }

    //Setup to sense up to 18 inches, max LED brightness
    byte ledBrightness = 0xFF; //Options: 0=Off to 255=50mA
    byte sampleAverage = 1;    //Options: 1, 2, 4, 8, 16, 32
    byte ledMode = 3;          //Options: 1 = Red only, 2 = Red + IR, 3 = Red + IR + Green
    int sampleRate = 50;       //Options: 50, 100, 200, 400, 800, 1000, 1600, 3200
    int pulseWidth = 69;       //Options: 69, 118, 215, 411
    int adcRange = 2048;       //Options: 2048, 4096, 8192, 16384

    //particleSensor.setup(ledBrightness, sampleAverage, ledMode, sampleRate, pulseWidth, adcRange); //Configure sensor with these settings
    particleSensor.setup();
    particleSensor.setPulseAmplitudeIR(0x24);

    //Pre-populate the plotter so that the Y scale is close to IR values
    display.begin(SSD1306_SWITCHCAPVCC, 0x3C); // initialize with the I2C addr 0x3D (for the 128x64)
    //display.display();                         // 屏幕显示（显示内容为预设画面）
    display.clearDisplay(); //清理屏幕和缓存区（I2C只清理缓存区）
    Draw_Init_Interface();
}

void loop()
{
    int i, j;
    MPU_starttime = millis();
    for (i = 0; i < BUFFERLEN; i++)
    {
        display.clearDisplay();
        display.setTextSize(1);  //设置字体大小
        display.setCursor(0, 5); //设置显示位置
        mpu6050.update();
        MPU_DATA[0][i] = mpu6050.getAngleX();
        MPU_DATA[1][i] = mpu6050.getAngleY();
        MPU_DATA[2][i] = mpu6050.getAngleZ();
        MPU_DATA[3][i] = mpu6050.getAccX();
        MPU_DATA[4][i] = mpu6050.getAccY();
        MPU_DATA[5][i] = mpu6050.getAccZ();
        display.print("X: ");
        display.print(MPU_DATA[0][i]);
        display.print("/");
        display.println(MPU_DATA[3][i]);
        display.print("Y: ");
        display.print(MPU_DATA[1][i]);
        display.print("/");
        display.println(MPU_DATA[4][i]);
        display.print("Z: ");
        display.print(MPU_DATA[2][i]);
        display.print("/");
        display.println(MPU_DATA[5][i]);
        //display.print("fps = ");
        //display.println(MPU_fps);
        display.display();
        Serial.print("X: ");
        Serial.print(MPU_DATA[0][i]);
        Serial.print("/");
        Serial.println(MPU_DATA[3][i]);
        Serial.print("Y: ");
        Serial.print(MPU_DATA[1][i]);
        Serial.print("/");
        Serial.println(MPU_DATA[4][i]);
        Serial.print("Z: ");
        Serial.print(MPU_DATA[2][i]);
        Serial.print("/");
        Serial.println(MPU_DATA[5][i]);
        Serial.print("fps = ");
        Serial.println(MPU_fps);
        display.display();
    }
    MPU_endtime = millis();
    MPU_fps = BUFFERLEN * 1000.0 / (MPU_endtime - MPU_starttime);

    SerialBT.print("MPU ");
    SerialBT.println(MPU_fps);
    for (i = 0; i < BUFFERLEN; i++)
    {
        for (j = 0; j < 6; j++)
        {
            SerialBT.print(MPU_DATA[j][i]);
            SerialBT.print(" ");
        }
        SerialBT.println();
    }
    delay(500);

    MAX_starttime = millis();
    for (i = 0; i < BUFFERLEN; i++) //do we have new data?
    {
        MAX_IR_DATA[i] = particleSensor.getIR();
        display.clearDisplay();
        display.setTextSize(1);  //设置字体大小
        display.setCursor(0, 5); //设置显示位置

        display.print("IR[");
        display.print(MAX_IR_DATA[i]);
        display.println("]");
        display.display();
        Serial.print("IR[");
        Serial.print(MAX_IR_DATA[i]);
        Serial.println("]");

        //Serial.print("Temp[");
        //Serial.print(particleSensor.readTemperature());
        //Serial.print("]");
        //Serial.println();
        //Serial.print("fps = ");
        //Serial.println(MAX_fps);
    }
    MAX_endtime = millis();
    MAX_fps = BUFFERLEN * 1000.0 / (MAX_endtime - MAX_starttime);

    SerialBT.print("MAX ");
    SerialBT.print(MAX_fps);
    for (i = 0; i < BUFFERLEN; i++)
    {
        SerialBT.print(MAX_IR_DATA[i]);
        SerialBT.println();
    }
    delay(500);

    Press_starttime = millis();
    for (i = 0; i < BUFFERLEN; i++)
    {
        Press_DATA[i] = analogRead(4);

        display.clearDisplay();
        display.setTextSize(1);  //设置字体大小
        display.setCursor(0, 5); //设置显示位置
        display.print("Press[");
        display.print(Press_DATA[i]);
        display.println("]");
        display.display();

        Serial.print("Press[");
        Serial.print(Press_DATA[i]);
        Serial.println("]");
    }
    Press_endtime = millis();
    Press_fps = BUFFERLEN * 1000.0 / (Press_endtime - Press_starttime);

    SerialBT.print("Press ");
    SerialBT.println(Press_fps);
    for (i = 0; i < BUFFERLEN; i++)
    {
        SerialBT.print(Press_DATA[i]);
        SerialBT.println();
    }
    //if (SerialBT.available)
    /*

    
    Serial.print("\tangleX : ");
    Serial.print(mpu6050.getAngleX());
    Serial.print("\tangleY : ");
    Serial.print(mpu6050.getAngleY());
    Serial.print("\tangleZ : ");
    Serial.println(mpu6050.getAngleZ());
    */
    /*
    if (checkForBeat(irValue) == true)
    {
        //We sensed a beat!
        Serial.println("Beating");
        long delta = millis() - lastBeat;
        lastBeat = millis();

        beatsPerMinute = 60 / (delta / 1000.0);

        if (beatsPerMinute < 255 && beatsPerMinute > 20)
        {
            rates[rateSpot++] = (byte)beatsPerMinute; //Store this reading in the array
            rateSpot %= RATE_SIZE;                    //Wrap variable

            //Take average of readings
            beatAvg = 0;
            for (byte x = 0; x < RATE_SIZE; x++)
                beatAvg += rates[x];
            beatAvg /= RATE_SIZE;
        }
    }
    */

    //Serial.println(irValue);
    //display.print("BPM=");
    //display.println(beatsPerMinute);
    //display.print("Avg BPM=");
    //display.println(beatAvg);
}
